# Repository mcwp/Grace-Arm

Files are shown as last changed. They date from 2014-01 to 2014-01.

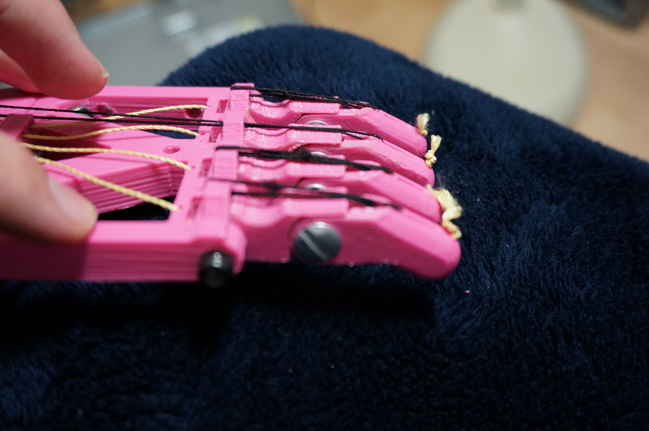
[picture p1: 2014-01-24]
009.JPG

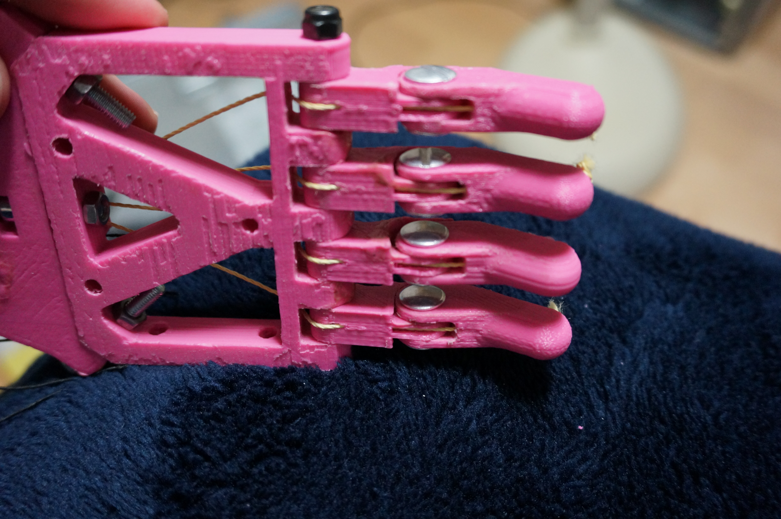
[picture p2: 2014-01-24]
010.JPG

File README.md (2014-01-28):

Grace-Arm
=========

This is a low cost prosthesis design for people with arms which end between the elbow and wrist. 

It uses ~1.5mm cabling (I'm using kevlar thread so far) and thin elastic thread to draw the fingers back. The fingers are actuated by the motion of the elbow.

Required Hardware:
-Cabling
-Thin elastic thread
-About 10 M4 8mm length Chicago screws from ChicagoScrews.com
-3d printed parts found here
-one M8 threaded rod to act as the prosthetic forearm. Length varies with user.
-one M5 threaded rod to aid M8 rod in forearm. Length equal to M8
-Four M8 nuts
-Four M5 nuts
-3 M4 Nylock Nuts
-one M4 rod cut to width of knuckles + two nylock nuts = 81 mm
-One M4x16 or M4x20 screw

Assembly:
-Print all pieces
-Sand all interfacing surfaces in the joints until they move smoothly
-Thread cabling through the holes in the bottom of the fingers before assembling *pictures coming soon*
-Assemble using chicago screws in the mid-finger joints and M4 rod/screws in the hand/finger joints.
-The chicago screws only need to be finger tight
-Thread one piece of elastic thread through the upper holes in each finger, then put both ends of the thread through the holes at the hand/finger knuckles. Finally, thread one end of the thread through one of the holes in the bar near the wrist, and tie the ends together to form a loop. Experiment with the tension in the elastic until the fingers pull back consistently.
-Tighten an M4 nylock onto each end of the M4 rod in the knuckles until the nylock is engaged. Don't actually tighten them down onto the plastic, or it will flex slightly and make the knuckles move less freely.
-Insert nuts into the nut traps of the wrist piece
-Screw nuts down onto the ends of the arm rods
-Screw arm rods in until tight
???????
-Figure out how to mount the other ends of the arm rods to the user's arm
-Find a way to attach the cables to the tricep region of the user's arm, ideally using a tensioning block found on the e-nable group.

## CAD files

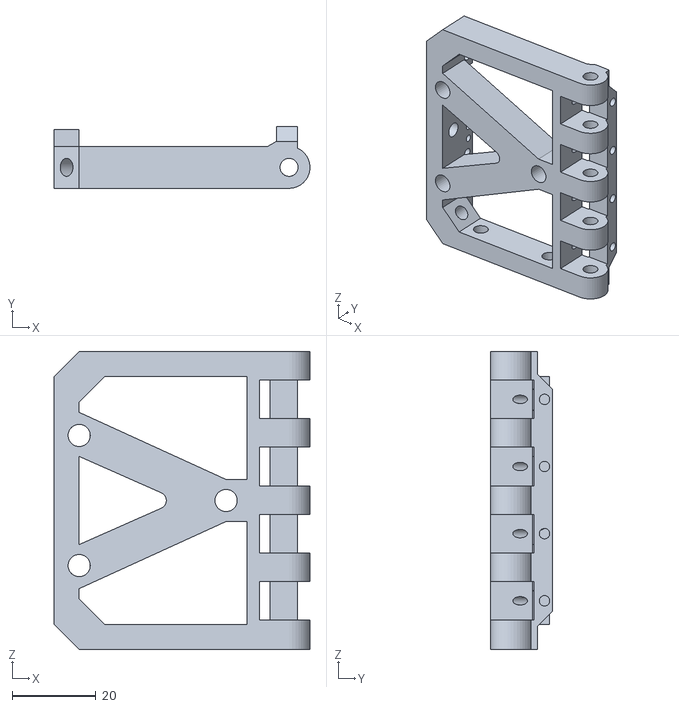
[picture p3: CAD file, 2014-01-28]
Palm structure.stl
61.0 x 14.7 x 71.0

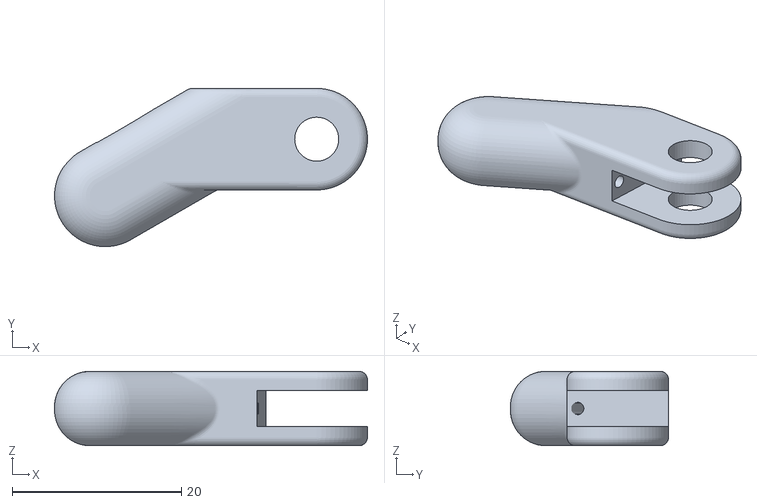
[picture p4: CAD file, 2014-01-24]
Finger distal.stl
37.0 x 18.7 x 8.80

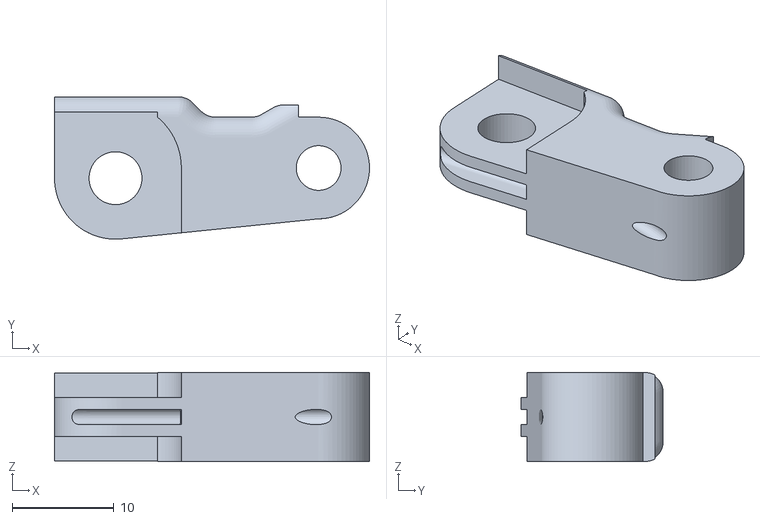
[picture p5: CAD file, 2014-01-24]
Finger proximal.stl
31.0 x 14.0 x 8.80

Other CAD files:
Palm structure left.stl

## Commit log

2014-01-24 Fingers and Palm structure published
    Uploaded .stls for the two finger segments and the palm structure.
    [Finger distal.stl, Finger proximal.stl, Palm structure.stl]
2014-01-24 Added left palm
    Mirrored palm added.
    [Palm structure left.stl]
2014-01-27 Added thumb, wrist, and updated palm structures.
    Added more distant elastic tie offs to the palm, and uploaded the thumb
    and wrist pieces.
    Note: All files currently have tolerances which work well for my
    printer. Tolerances can be adjusted for people, and inventor files
    provided by request.
    [Palm structure left.stl, Palm structure.stl, Thumb mount.stl, Thumb proximal.stl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]
2014-01-27 Revert "Added thumb, wrist, and updated palm structures."
    This reverts commit 2d8086f84f6b2081a6bb1e44b908b2eca28f01a0.
    [Palm structure left.stl, Palm structure.stl, Thumb mount.stl, Thumb proximal.stl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]
2014-01-27 Adde thumb, wrist, and updated palm structures.
    Added elastic tie offs back by the wrist to palm structures, so that the
    % change in length of the elastic is reduced. This produces a more
    constant retracting force.
    Also uploaded wrist and thumb parts. Note: Thumb can be replaced easily
    with alternative angles.
    [Palm structure left.stl, Palm structure.stl]
2014-01-28 Fixed Palm structures
    I accidentally uploaded an old version.
    [Palm structure left.stl, Palm structure.stl]
